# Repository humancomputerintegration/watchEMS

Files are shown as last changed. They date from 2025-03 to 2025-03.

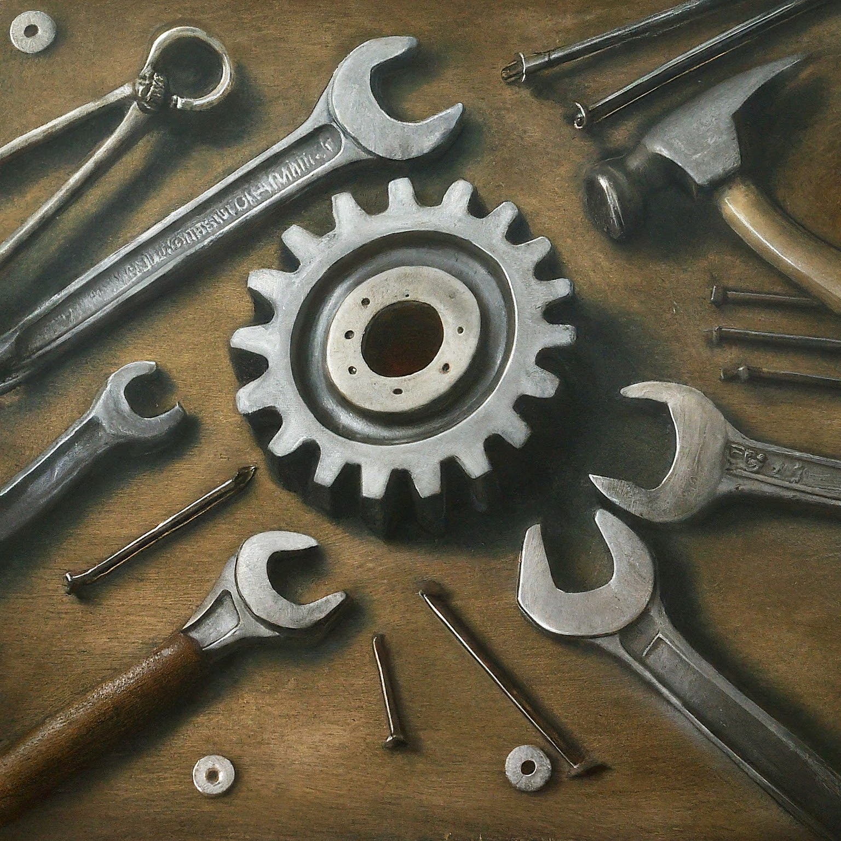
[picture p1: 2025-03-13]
codes/PCVersions/ManualCalibration/img.jpeg

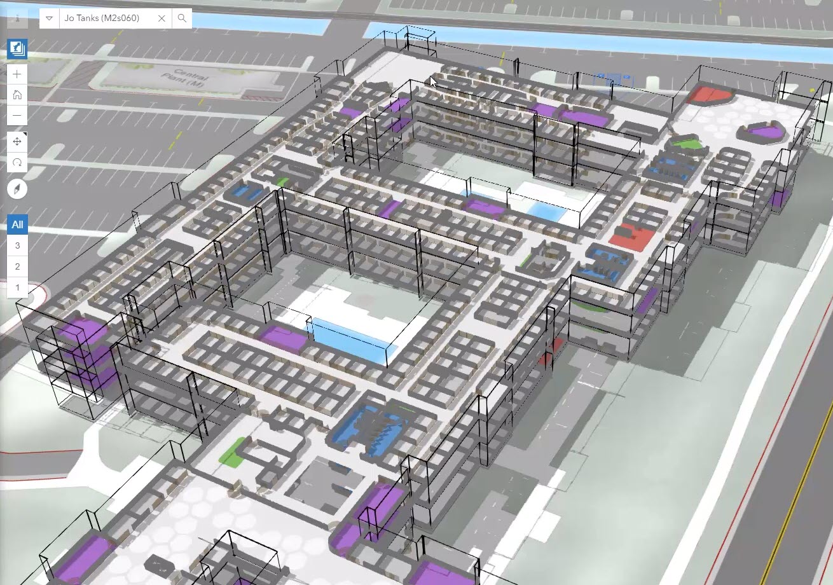
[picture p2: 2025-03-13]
codes/PCVersions/WizardOfOZMaps(Indoor)/img.jpg

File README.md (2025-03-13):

# Can a Smartwatch Move Your Fingers? 

This repository contains the source code used in the research publication "Can a Smartwatch Move Your Fingers?" from the [Human-Computer Integration Lab](https://lab.plopes.org/) at the University of Chicago.

## Citing

When using or building upon this device in an academic publication, please consider citing as follows:

ACM Reference Format: Akifumi Takahashi, Yudai Tanaka, Archit Tamhane, Alan Shen, Shan-Yuan Teng, and Pedro Lopes. 2024. Can a Smartwatch Move Your Fingers? Compact and Practical Electrical Muscle Stimulation in a Smartwatch. In The 37th Annual ACM Symposium on User Interface Software and Technology (UIST ’24), October 13–16, 2024, Pittsburgh, PA, USA. ACM, New York, NY, USA, 15 pages. https://doi.org/10.1145/3654777.3676373

## Contact

For any questions about this repository, please contact yudaitanaka@uchicago.edu

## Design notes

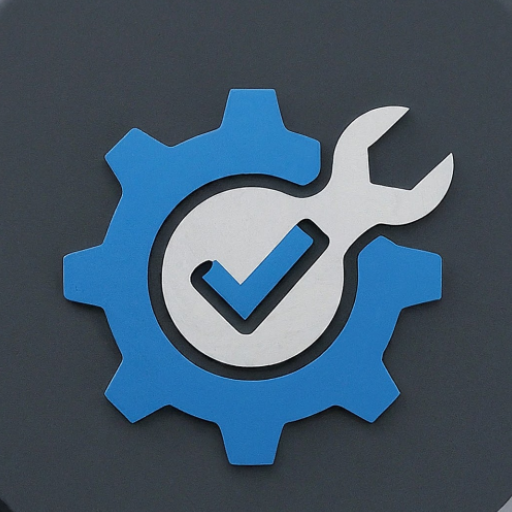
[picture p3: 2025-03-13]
codes/PCVersions/CalibApp/ic_launcher-playstore.png

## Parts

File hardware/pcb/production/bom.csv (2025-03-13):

Designator | Footprint | Quantity | Value | LCSC Part #
C1, C18 | 0402 | 2 | 1nF | C1523
C10 | 0402 | 1 | 220pF | C1530
C11, C12, C13, C14 | 0805 | 4 | 100nF | C5331016
C15, C16 | 0402 | 2 | 100nF | C9900048290
C17 | 0402 | 1 | 10uF | C408132
C19, C20 | 0603 | 2 | 4.7uF | C19666
C2, C22, C23, C3, C4, C8 | 1206 | 6 | 47uF | C76659
C21 | 0402 | 1 | 120pF | C695379
C5 | 0402 | 1 | 0.1uF | C1525
C6 | 0402 | 1 | 22nF | C1532
C7 | 0402 | 1 | 100pF | C1546
C9 | 0402 | 1 | 10nF | C15195
D1 | RF081MM2STR | 1 | RF081MM2STR | C509966
D2 | SOD2512X110N | 1 | NSVR1020MW2T1G | C893984
IC1, IC10, IC11, IC12, IC13, IC14, IC15, IC16, IC17, IC18, IC19, IC2, IC20, IC21, IC22, IC23, IC24, IC3, IC4, IC5, IC6, IC7, IC8, IC9 | SOP254P700X220-4N | 24 | TLP188_TPL,E | C4153840
IC25 | SOIC127P600X175-8N | 1 | DAC8830ID | C42816
IC26 | SOP65P640X120-14N | 1 | OPA4205APWT | C20345595
J1 | JST_GH_SM02B-GHS-TB_1x02-1MP_P1.25mm_Horizontal | 1 | Conn_01x02_Pin | C189893
J10, J8, J9 | PinHeader_1x04_P2.54mm_Vertical | 3 | Conn_01x04_Pin
J11, J12, J13, J2, J3, J4, J5, J6, J7 | Molex_200528-0070_1x07-1MP_P1.00mm_Horizontal | 9 | Conn_01x07_Pin | C6369987
JP3 | SolderJumper-2_P1.3mm_Open_TrianglePad1.0x1.5mm | 1 | Jumper_2_Open
L1 | 1008 | 1 | 4.7uH | C668313
L2 | 1008 | 1 | 1uH | C435392
Q1 | SOT95P280X100-3N | 1 | RSR030N06TL | C126317
Q2, Q4, Q5 | SOT96P237X111-3N | 3 | MMBTA92LT1G | C82049
Q3 | SOT-23 | 1 | DMN30H4D0L | C461015
R1, R2, R29, R49 | 0402 | 4 | 100k | C25741
R10, R11, R12, R13, R14, R15, R16, R17, R18, R19, R20, R21, R22, R23, R24, R25, R26, R27, R4, R5, R6, R7, R8, R9 | 0402 | 24 | 330 | C25104
R28 | 0402 | 1 | 130k(100kHz) | C409851
R3 | 0402 | 1 | 2k | C4109
R30 | 0402 | 1 | 240k | C413113
R31 | 0402 | 1 | 6.8k | C409870
R32, R34, R47 | 0402 | 3 | 22 | C413049
R33 | 0603 | 1 | 0.02 | C2088537
R35, R36, R37 | 0402 | 3 | 499k | C2986233
R38 | 0402 | 1 | 16k | C409889
R39 | 0402 | 1 | 300k | C131560
R40 | 0402 | 1 | 200k | C131534
R41 | 0402 | 1 | 1k | C445596
R42 | 0402 | 1 | 1k3 | C336808
R43 | 0402 | 1 | 100 | C491157
R44 | 0402 | 1 | 1M | C413126
R45 | 0402 | 1 | 30k | C413010
R46 | 0402 | 1 | 100 | C25077
R48 | 0402 | 1 | 453k | C27009
R50 | 0402 | 1 | 499k | C25793
T1 | ATB3225150110T000 | 1 | ATB322515-0110-T000 | C415291
U1 | SOT-23-5 | 1 | MCP73812T-420I-OT | C144308
U2 | XIAO-nRF52840-Sense-14P-2.54-21X17.8MM)_onlyPins | 1 | SeeeduinoXIAO_onlyPinHeader
U3, U4, U5 | SOP65P640X110-16N | 3 | 74AHCT595 | C554707
U6 | MSOP-10-1EP_3x3mm_P0.5mm_EP1.68x1.88mm | 1 | LT3757AEMSE | C671465
U7 | SOTFL50P160X60-6N | 1 | XPS62A01DRLR | C5157937
U8 | SOT-23-5 | 1 | TPS613222ADBV | C2071163
ffc calble | 7pin pitch1mm 30mm |  | 0152670745 |  | Molex | 0152670745 | https://www.digikey.com/en/products/detail/molex/0152670745/4427495
ffc calble | 7pin pitch1mm 50mm |  | 0152670747 |  | Molex | 0152670747 | https://www.digikey.com/en/products/detail/molex/0152670747/4427497
ffc calble | 7pin pitch1mm 70mm |  | 0151670749 |  | Molex | 0151670749 | https://www.digikey.com/en/products/detail/molex/0151670749/4426466
ffc calble | 7pin pitch1mm 76mm |  | 10-07-A-0076-C-4-08-4-T |  | GCT | 10-07-A-0076-C-4-08-4-T | https://www.digikey.jp/ja/products/detail/gct/10-07-A-0076-C-4-08-4-T/22247725
ffc calble | 7pin pitch1mm 50mm |  | 10-07-A-0050-C-4-08-4-T |  | GCT | 10-07-A-0050-C-4-08-4-T | https://www.digikey.jp/ja/products/detail/gct/10-07-A-0050-C-4-08-4-T/22247681
ffc calble | 7pin pitch1mm 152mm |  | 10-07-A-0152-C-4-08-4-T |  | GCT | 10-07-A-0152-C-4-08-4-T | https://www.digikey.jp/ja/products/detail/gct/10-07-A-0152-C-4-08-4-T/22247734
ffc calble | 7pin pitch1mm 100mm |  | 10-07-A-0101-C-4-08-4-T |  | GCT | 10-07-A-0101-C-4-08-4-T | https://www.digikey.jp/ja/products/detail/gct/10-07-A-0101-C-4-08-4-T/22247600
battery |  |  |  |  |  |  | https://www.amazon.com/gp/product/B09WK78594/ref=ppx_yo_dt_b_asin_title_o01_s00?ie=UTF8&psc=1
 |  |  | DTP401525(EZ3) |  |  |  | https://www.marutsu.co.jp/pc/i/2228265/
J1 |  |  | SM02B-SRSS-TB |  |  | SM02B-SRSS-TB | https://www.digikey.jp/ja/products/detail/jst-sales-america-inc/SM02B-SRSS-TB/926708
J1 housing |  |  | SHR-02V-S-B |  |  | SHR-02V-S-B | https://www.digikey.jp/ja/products/detail/jst-sales-america-inc/SHR-02V-S-B/759866

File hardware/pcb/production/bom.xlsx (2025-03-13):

Designator | Footprint | Quantity | Value | require | LCSC Part # |  |  |  |  | Quantity | rate | total | price/1 | price total
C1, C2, C3, C4 | CAPC2012X145N | 4 | 68nF | 200V |  | TDK | CGJ4J3X7T2D683K125AA | https://www.digikey.com/en/products/detail/tdk-corporation/CGJ4J3X7T2D683K125AA/3673570 |  | 4 | 3 | 12 | 0.64 | 7.68
C5 | 0201(0603) | 1 | 220pF | 25V |  | TDK | CGA1A2X7R1E221K030BA | https://www.digikey.com/en/products/detail/tdk-corporation/CGA1A2X7R1E221K030BA/3949331 |  | 1 | 10 | 10 | 0.1 | 1
C6 | 0201(0603) | 1 | 10nF | 25V |  | TDK | GRM033R61E103MA12D (https://www.digikey.com/en/products/detail/murata-electronics/GRM033R61E103MA12D/4904729) | https://www.digikey.com/en/products/detail/murata-electronics/GRM033R61E103MA12D/4904730 |  | 1 | 10 | 10 | 0.1 | 1
C7 | 0201(0603) | 1 | 0.1uF | 16V |  | TDK | C0603X5R1E104K030BB | https://www.digikey.com/en/products/detail/tdk-corporation/C0603X5R1E104K030BB/3950907 |  | 1 | 10 | 10 | 0.1 | 1
C8 | 0201(0603) | 1 | 22nF | 16V |  | TDK | C0603X5R1E223K030BB | https://www.digikey.com/en/products/detail/tdk-corporation/C0603X5R1E223K030BB/3950911 |  | 1 | 10 | 10 | 0.1 | 1
C9 | 0201(0603) | 1 | 1nF | 16V |  | TDK | C0603X7R1E102K030BA | https://www.digikey.com/en/products/detail/tdk-corporation/C0603X7R1E102K030BA/2732710 |  | 1 | 10 | 10 | 0.1 | 1
D1 | RF081MM2STR | 1 | RF081MM2STR | 200V |  | Rohm Semiconductor | RF081MM2STR | https://www.digikey.com/en/products/detail/rohm-semiconductor/RF081MM2STR/5001871 | 200V 800MA | 1 | 3 | 3 | 0.48 | 1.44
IC1, IC10, IC11, IC12, IC13, IC14, IC15, IC16, IC17, IC18, IC19, IC2, IC20, IC21, IC22, IC23, IC24, IC25, IC26, IC27, IC28, IC29, IC3, IC30, IC31, IC32, IC4, IC5, IC6, IC7, IC8, IC9 | SOP254P700X220-4N | 32 | TLP188_TPL,E | 200V |  | Toshiba Semiconductor and Storage | TLP188(TPL,E | https://www.digikey.com/en/products/detail/toshiba-semiconductor-and-storage/TLP188-TPL-E/4562859 | OPTOISO 3.75KV TRANS 6-SO 4 LEAD | 32 | 1 | 32 | 0.81 | 25.92
IC33 | SOIC127P599X175-8N | 1 | LT1013DS8#TRPBF |  |  | Analog Devices Inc. | LT1013DS8#TRPBF | https://www.digikey.com/en/products/detail/analog-devices-inc/LT1013DS8-TRPBF/960372 |  | 1 | 3 | 3 | 7.28 | 21.84
J1, J11, J12, J14, J3, J5, J6, J8, J9 | Molex_200528-0070_1x07-1MP_P1.00mm_Horizontal | 9 | Conn_01x07_Pin |  |  | Molex | 2005280070 | https://www.digikey.com/en/products/detail/molex/2005280070/6099557 |  | 9 | 3 | 27 | 0.6 | 16.2
J10, J15, J2, J4, J7 | PinHeader_1x04_P2.54mm_Vertical | 5 | Conn_01x04_Pin |  |  |  |  |  |  | 5 | 3 | 15 |  | 0
JP1 | SolderJumper-2_P1.3mm_Open_TrianglePad1.0x1.5mm | 1 | Jumper_2_Open |  |  |  |  |  |  | 1 | 3 | 3 |  | 0
JP2 | SolderJumper-3_P2.0mm_Open_TrianglePad1.0x1.5mm_NumberLabels | 1 | Jumper_3_Open |  |  |  |  |  |  | 1 | 3 | 3 |  | 0
Q1 | SOT95P280X100-3N | 1 | RQ5E030AJTCL -> SSM3K376R,LF | 30V |  | Toshiba Semiconductor and Storage | SSM3K376R,LF | https://www.digikey.com/en/products/detail/toshiba-semiconductor-and-storage/SSM3K376R-LF/9472331?s=N4IgTCBcDaIMpwLIGYDSyDsA2ASgGgBkAxEAXQF8g | 30V4A | 1 | 3 | 3 | 0.38 | 1.14
Q2 | SOT-23 | 1 | DMN24H11DS | 200V |  | Diodes Incorporated | DMN24H11DS-7 | https://www.digikey.com/en/products/detail/diodes-incorporated/DMN24H11DS-7/9770107 |  | 1 | 3 | 3 | 0.44 | 1.32
Q3, Q4, Q5 | SOT96P237X111-3N | 3 | MMBTA92LT1G | 200V |  | onsemi | MMBTA92LT3G | https://www.digikey.com/en/products/detail/onsemi/MMBTA92LT3G/1481979 | TRANS PNP 300V 0.5A SOT23-3 | 3 | 3 | 9 | 0.21 | 1.89
R1 | 0201(0603) | 1 | 100k | 1.1e-4W |  | Panasonic Electronic Components | ERJ-1GNF1003C | https://www.digikey.com/en/products/detail/panasonic-electronic-components/ERJ-1GNF1003C/2036340?s=N4IgTCBcDaIKICUBSBaAjAcQHIDE0AZ8BmAYRAF0BfIA |  | 1 | 10 | 10 | 0.1 | 1
R10, R11, R12, R13, R14, R15, R16, R17, R18, R19, R20, R21, R22, R23, R24, R25, R26, R27, R28, R29, R30, R31, R32, R33, R34, R35, R36, R37, R38, R39, R40, R41 | 0201(0603) | 32 | 470 -> 220 |  |  | Panasonic Electronic Components | ERJ-1GNF4700C | https://www.digikey.com/en/products/detail/panasonic-electronic-components/erj-1gnf2200c/2036034 |  | 32 | 2 | 64 | 0.1 | 6.4
R2, R4 | 0201(0603) | 2 | 22 | 1e-5W |  | Panasonic Electronic Components | ERJ-1GNF22R0C | https://www.digikey.com/en/products/detail/panasonic-electronic-components/ERJ-1GNF22R0C/2035920 | RES SMD 22 OHM 1% 1/20W 0201 | 2 | 10 | 20 | 0.1 | 2
R3 | 0201(0603) | 1 | 47k |  |  | Panasonic Electronic Components | ERJ-1GNF4702C | https://www.digikey.com/en/products/detail/panasonic-electronic-components/ERJ-1GNF4702C/2036302 |  | 1 | 10 | 10 | 0.1 | 1
R42 | 0201(0603) | 1 | 3,3k | 0.024W |  | Panasonic Electronic Components | ERJ-1GNF3301C | https://www.digikey.com/en/products/detail/panasonic-electronic-components/ERJ-1GNF3301C/2036169 |  | 1 | 10 | 10 | 0.1 | 1
R43 | 0201(0603) | 1 | 10k | 0.01W(MOSFET broken 0.066W) |  | Panasonic Electronic Components | ERJ-1GNF1002C (https://www.digikey.com/en/products/detail/panasonic-electronic-components/ERJ-1GNF1002C/2036226) | https://www.digikey.com/en/products/detail/panasonic-electronic-components/ERJ-1GNF1002C/2036226 |  | 1 | 10 | 10 | 0.1 | 1
R44 | 0603 (1608) | 1 | 1k | 0.1W |  | Panasonic Electronic Components | ERJ-PB3D1001V | https://www.digikey.com/en/products/detail/panasonic-electronic-components/ERJ-PB3D1001V/6213066 | 2 kOhms ±0.5% 0.2W, 1/5W Chip Resistor 0603 (1608 Metric) Automotive AEC-Q200, Pulse Withstanding Thick Film | 1 | 10 | 10 | 0.16 | 1.6
R45, R5 | 0402 (1005) | 2 | 1M | 0.01W |  | Panasonic Electronic Components | ERJ-2RKF1004X | https://www.digikey.com/en/products/detail/panasonic-electronic-components/ERJ-2RKF1004X/79728 |  | 2 | 10 | 20 | 0.1 | 2
R46 | 0201(0603) | 1 | 25k -> 30k | 2.37e-4W |  | Panasonic Electronic Components | ERJ-1GNF3002C | https://www.digikey.com/en/products/detail/panasonic-electronic-components/ERJ-1GNF3002C/2036278 |  | 1 | 10 | 10 | 0.1 | 1
R47 | 0201(0603) | 1 | 100 |  |  | Panasonic Electronic Components | ERJ-1GNF1000C | https://www.digikey.com/en/products/detail/panasonic-electronic-components/ERJ-1GNF1000C/2035998 |  | 1 | 10 | 10 | 0.1 | 1
R6 | 0201(0603) | 1 | 6.8k |  |  | Panasonic Electronic Components | ERJ-1GNF6801C | https://www.digikey.com/en/products/detail/panasonic-electronic-components/ERJ-1GNF6801C/2036207 |  | 1 | 10 | 10 | 0.1 | 1
R7 | 0603 (1608) | 1 | 0.02 | 1/3W |  | Panasonic Electronic Components | ERJ-3BWFR020V | https://www.digikey.com/en/products/detail/panasonic-electronic-components/ERJ-3BWFR020V/5647494 | 20 mOhms ±1% 0.333W, 1/3W Chip Resistor 0603 (1608 Metric) | 1 | 10 | 10 | 0.36 | 3.6
R8 | 0201(0603) | 1 | 16k | 2.5e-6W |  | Panasonic Electronic Components | ERJ-1GNF1602C | https://www.digikey.com/en/products/detail/panasonic-electronic-components/ERJ-1GNF1602C/2036247 |  | 1 | 10 | 10 | 0.1 | 1
R9 | 0201(0603) | 1 | 130k(100kHz) or 41.2k(300kHz) |  |  | Panasonic Electronic Components | ERJ-1GNF1303C | https://www.digikey.com/en/products/detail/panasonic-electronic-components/ERJ-1GNF1303C/2036352 |  | 1 | 10 | 10 | 0.1 | 1
T1 | ATB3225150110T000 | 1 | ATB322515-0110-T000 |  |  | TDK | ATB322515-0110 | https://www.digikey.com/en/products/detail/tdk-corporation/ATB322515-0110/3008141?s=N4IgTCBcDaIIIBUBCBmMYCsBGDBaADFlvrgvuSALoC%2BQA |  | 1 | 3 | 3 | 2.12 | 6.36
U1 | MSOP-10-1EP_3x3mm_P0.5mm_EP1.68x1.88mm | 1 | LT3757AEMSE |  |  | Analog Devices Inc. | LT3757AEMSE#TRPBF | https://www.digikey.com/en/products/detail/analog-devices-inc/LT3757AEMSE-TRPBF/3838478 |  | 1 | 3 | 3 | 6.66 | 19.98
U2 | XIAO-nRF52840-Sense-14P-2.54-21X17.8MM)_onlyPins | 1 | SeeeduinoXIAO_onlyPinHeader |  |  |  |  |  |  | 1 | 3 | 3 |  | 0
U3, U4, U5, U6 | SOP65P640X110-16N | 4 | 74AHCT595 |  |  | Nexperia USA Inc. | 74AHCT595PW,118 | https://www.digikey.com/en/products/detail/nexperia-usa-inc/74AHCT595PW-118/1229738 |  | 4 | 3 | 12 | 0.58 | 6.96
ffc calble | 7pin pitch1mm 30mm | 4 | 0152670745 |  |  | Molex | 0152670745 | https://www.digikey.com/en/products/detail/molex/0152670745/4427495 |  | 4 | 3 | 12 | 1.41 | 16.92
ffc calble | 7pin pitch1mm 50mm | 4 | 0152670747 |  |  | Molex | 0152670747 | https://www.digikey.com/en/products/detail/molex/0152670747/4427497 |  | 4 | 3 | 12 | 1.62 | 19.44
ffc calble | 7pin pitch1mm 70mm | 4 | 0151670749 |  |  | Molex | 0151670749 | https://www.digikey.com/en/products/detail/molex/0151670749/4426466 |  | 4 | 3 | 12 | 1.35 | 16.2
 |  |  |  |  |  |  |  |  |  |  |  |  |  | 192.89

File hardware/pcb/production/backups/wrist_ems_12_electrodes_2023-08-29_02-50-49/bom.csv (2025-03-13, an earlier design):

Designator | Footprint | Quantity | Value | LCSC Part #
C1, C2, C3, C4 | CAPC2012X145N | 4 | 68nF
C5 | 0201 | 1 | 220pF
C6 | 0201 | 1 | 10nF
C7 | 0201 | 1 | 0.1uF
C8 | 0201 | 1 | 22nF
C9 | 0201 | 1 | 1nF
D1 | RF081MM2STR | 1 | RF081MM2STR
IC1, IC10, IC11, IC12, IC13, IC14, IC15, IC16, IC17, IC18, IC19, IC2, IC20, IC21, IC22, IC23, IC24, IC25, IC26, IC27, IC28, IC29, IC3, IC30, IC31, IC32, IC4, IC5, IC6, IC7, IC8, IC9 | SOP254P700X220-4N | 32 | TLP188_TPL,E
IC33 | SOIC127P599X175-8N | 1 | LT1013DS8#TRPBF
J1, J11, J12, J14, J3, J5, J6, J8, J9 | Molex_200528-0070_1x07-1MP_P1.00mm_Horizontal | 9 | Conn_01x07_Pin
J10, J15, J2, J4, J7 | PinHeader_1x04_P2.54mm_Vertical | 5 | Conn_01x04_Pin
JP1 | SolderJumper-2_P1.3mm_Open_TrianglePad1.0x1.5mm | 1 | Jumper_2_Open
JP2 | SolderJumper-3_P2.0mm_Open_TrianglePad1.0x1.5mm_NumberLabels | 1 | Jumper_3_Open
Q1 | SOT95P280X100-3N | 1 | RQ5E030AJTCL
Q2 | SOT-23 | 1 | DMN24H11DS
Q3, Q4, Q5 | SOT96P237X111-3N | 3 | MMBTA92LT1G
R1 | 0201 | 1 | 100k
R10, R11, R12, R13, R14, R15, R16, R17, R18, R19, R20, R21, R22, R23, R24, R25, R26, R27, R28, R29, R30, R31, R32, R33, R34, R35, R36, R37, R38, R39, R40, R41 | 0201 | 32 | 470
R2, R4 | 0201 | 2 | 22
R3 | 0201 | 1 | 47k
R42 | 0201 | 1 | 3,3k
R43 | 0201 | 1 | 10k
R44 | 0201 | 1 | 1k
R45, R5 | 0201 | 2 | 1M
R46 | 0201 | 1 | 25k
R47 | 0201 | 1 | 100
R6 | 0201 | 1 | 6.8k
R7 | 0201 | 1 | 0.02
R8 | 0201 | 1 | 16k
R9 | 0201 | 1 | 130k(100kHz) or 41.2k(300kHz)
T1 | ATB3225150110T000 | 1 | ATB322515-0110-T000
U1 | MSOP-10-1EP_3x3mm_P0.5mm_EP1.68x1.88mm | 1 | LT3757AEMSE
U2 | XIAO-nRF52840-Sense-14P-2.54-21X17.8MM)_onlyPins | 1 | SeeeduinoXIAO_onlyPinHeader
U3, U4, U5, U6 | SOP65P640X110-16N | 4 | 74AHCT595

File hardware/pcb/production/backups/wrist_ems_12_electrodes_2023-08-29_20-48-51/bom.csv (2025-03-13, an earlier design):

Designator | Footprint | Quantity | Value | LCSC Part #
C1 | 0201 | 1 | 0.1uF
C2 | 0201 | 1 | 22nF
C3 | 0201 | 1 | 1nF
C4 | 0201 | 1 | 220pF
C5 | 0201 | 1 | 10nF
C6, C7, C8, C9 | CAPC2012X145N | 4 | 68nF
D1 | RF081MM2STR | 1 | RF081MM2STR
IC1 | SOIC127P599X175-8N | 1 | LT1013DS8#TRPBF
IC10, IC11, IC12, IC13, IC14, IC15, IC16, IC17, IC18, IC19, IC2, IC20, IC21, IC22, IC23, IC24, IC25, IC26, IC27, IC28, IC29, IC3, IC30, IC31, IC32, IC33, IC4, IC5, IC6, IC7, IC8, IC9 | SOP254P700X220-4N | 32 | TLP188_TPL,E
J1, J11, J12, J13, J14, J3, J4, J5, J6 | Molex_200528-0070_1x07-1MP_P1.00mm_Horizontal | 9 | Conn_01x07_Pin
J10, J2, J7, J8, J9 | PinHeader_1x04_P2.54mm_Vertical | 5 | Conn_01x04_Pin
JP1 | SolderJumper-2_P1.3mm_Open_TrianglePad1.0x1.5mm | 1 | Jumper_2_Open
JP2 | SolderJumper-3_P2.0mm_Open_TrianglePad1.0x1.5mm_NumberLabels | 1 | Jumper_3_Open
Q1 | SOT95P280X100-3N | 1 | RQ5E030AJTCL
Q2, Q4, Q5 | SOT96P237X111-3N | 3 | MMBTA92LT1G
Q3 | SOT-23 | 1 | DMN24H11DS
R1 | 0201 | 1 | 130k(100kHz) or 41.2k(300kHz)
R10 | 0603 | 1 | 0.02
R11 | 0603 | 1 | 1k
R12 | 0402 | 1 | 1M
R13 | 0201 | 1 | 25k
R14 | 0201 | 1 | 1M
R15 | 0201 | 1 | 16k
R16, R17, R18, R19, R20, R21, R22, R23, R24, R25, R26, R27, R28, R29, R30, R31, R32, R33, R34, R35, R36, R37, R38, R39, R40, R41, R42, R43, R44, R45, R46, R47 | 0201 | 32 | 470
R2 | 0201 | 1 | 100k
R3 | 0201 | 1 | 47k
R4 | 0201 | 1 | 6.8k
R5 | 0201 | 1 | 100
R6, R7 | 0201 | 2 | 22
R8 | 0201 | 1 | 10k
R9 | 0201 | 1 | 3,3k
T1 | ATB3225150110T000 | 1 | ATB322515-0110-T000
U1 | MSOP-10-1EP_3x3mm_P0.5mm_EP1.68x1.88mm | 1 | LT3757AEMSE
U2 | XIAO-nRF52840-Sense-14P-2.54-21X17.8MM)_onlyPins | 1 | SeeeduinoXIAO_onlyPinHeader
U3, U4, U5, U6 | SOP65P640X110-16N | 4 | 74AHCT595

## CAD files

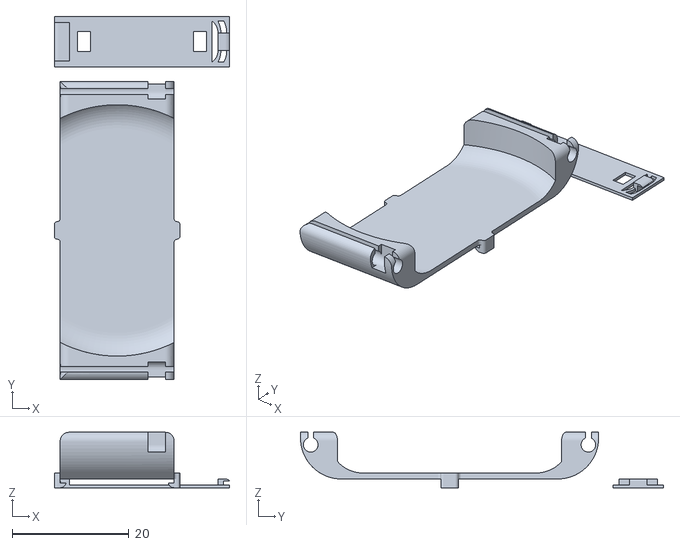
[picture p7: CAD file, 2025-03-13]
hardware/3dprinting/watch_mount v5.stl
30.0 x 62.1 x 9.50

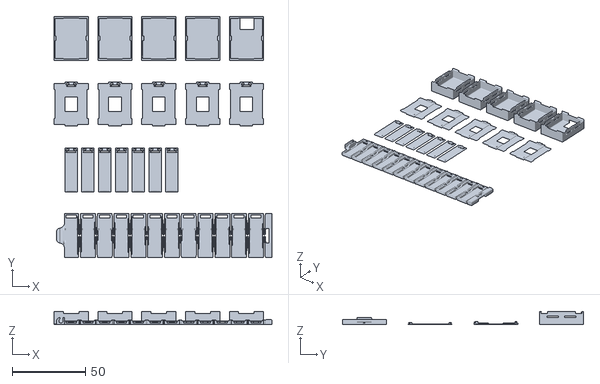
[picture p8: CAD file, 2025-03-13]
hardware/3dprinting/wristband_expandable_146.5(mm) v16.stl
149.2 x 165.0 x 9.00

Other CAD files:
hardware/3dprinting/watch_mount v4.stl
hardware/3dprinting/watch_mount v5.f3d
hardware/3dprinting/wristband_expandable_146.5(mm) v16.f3d

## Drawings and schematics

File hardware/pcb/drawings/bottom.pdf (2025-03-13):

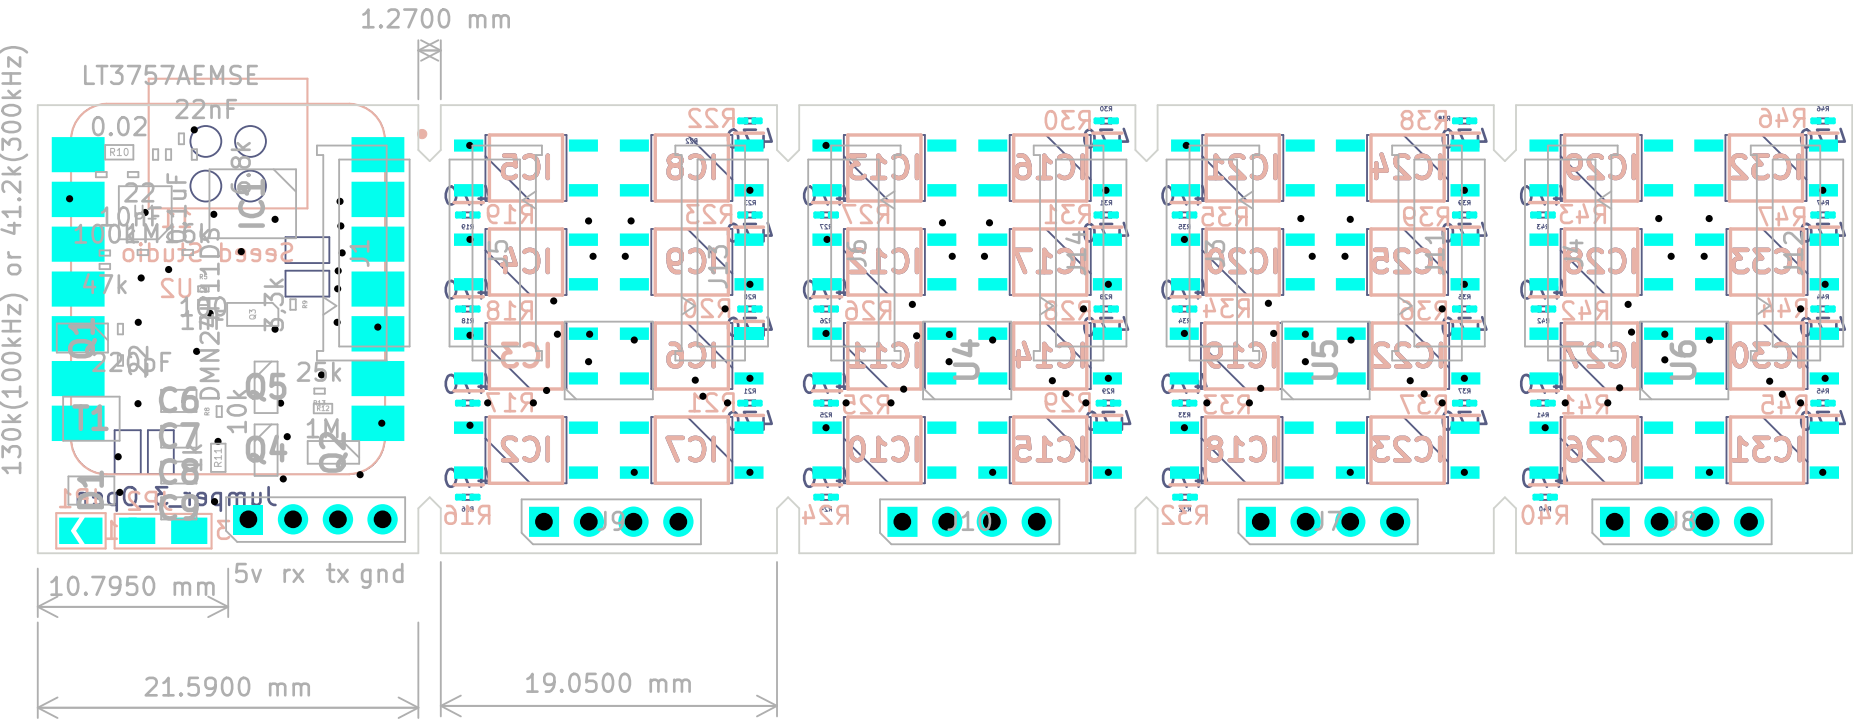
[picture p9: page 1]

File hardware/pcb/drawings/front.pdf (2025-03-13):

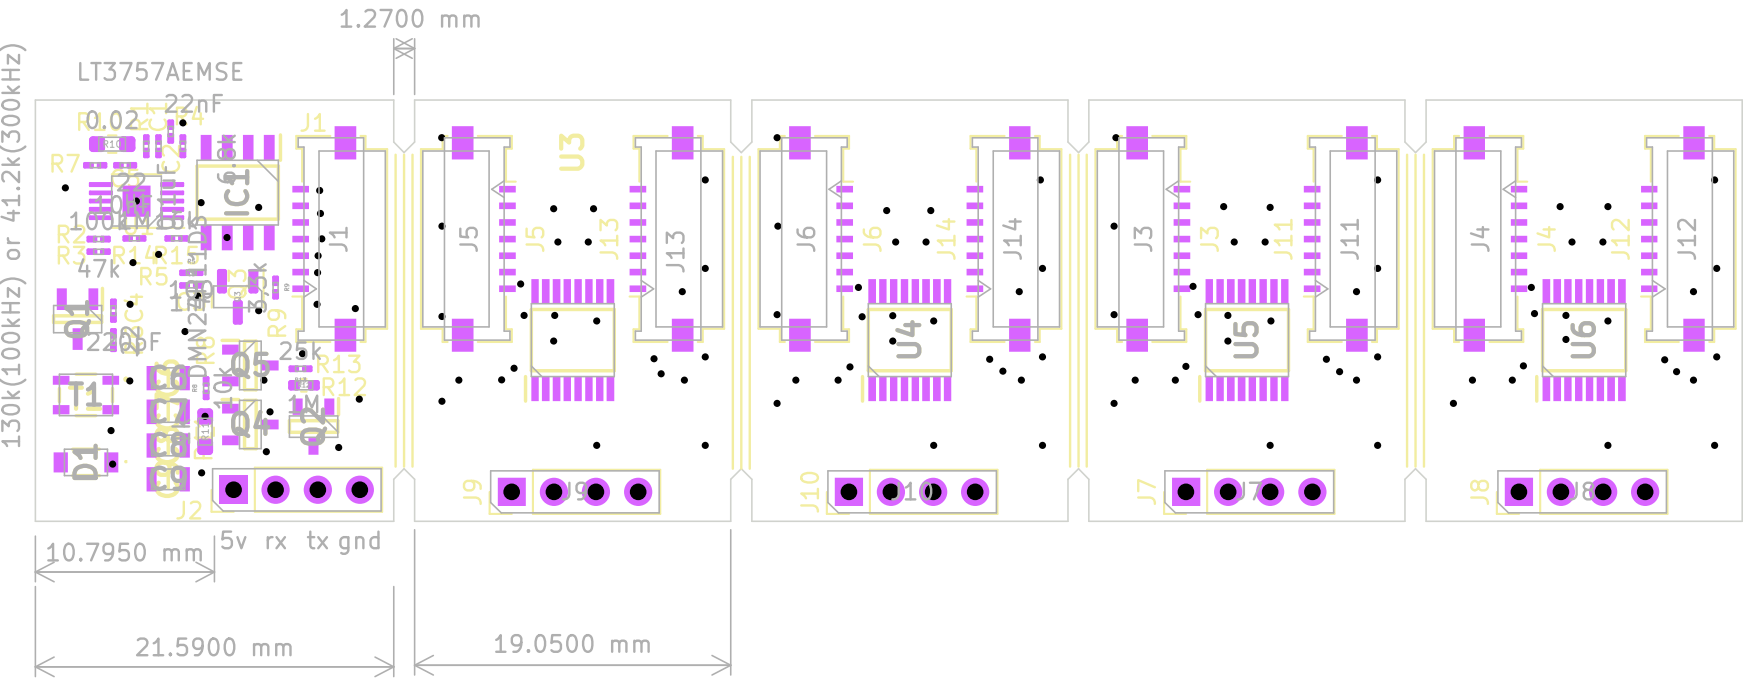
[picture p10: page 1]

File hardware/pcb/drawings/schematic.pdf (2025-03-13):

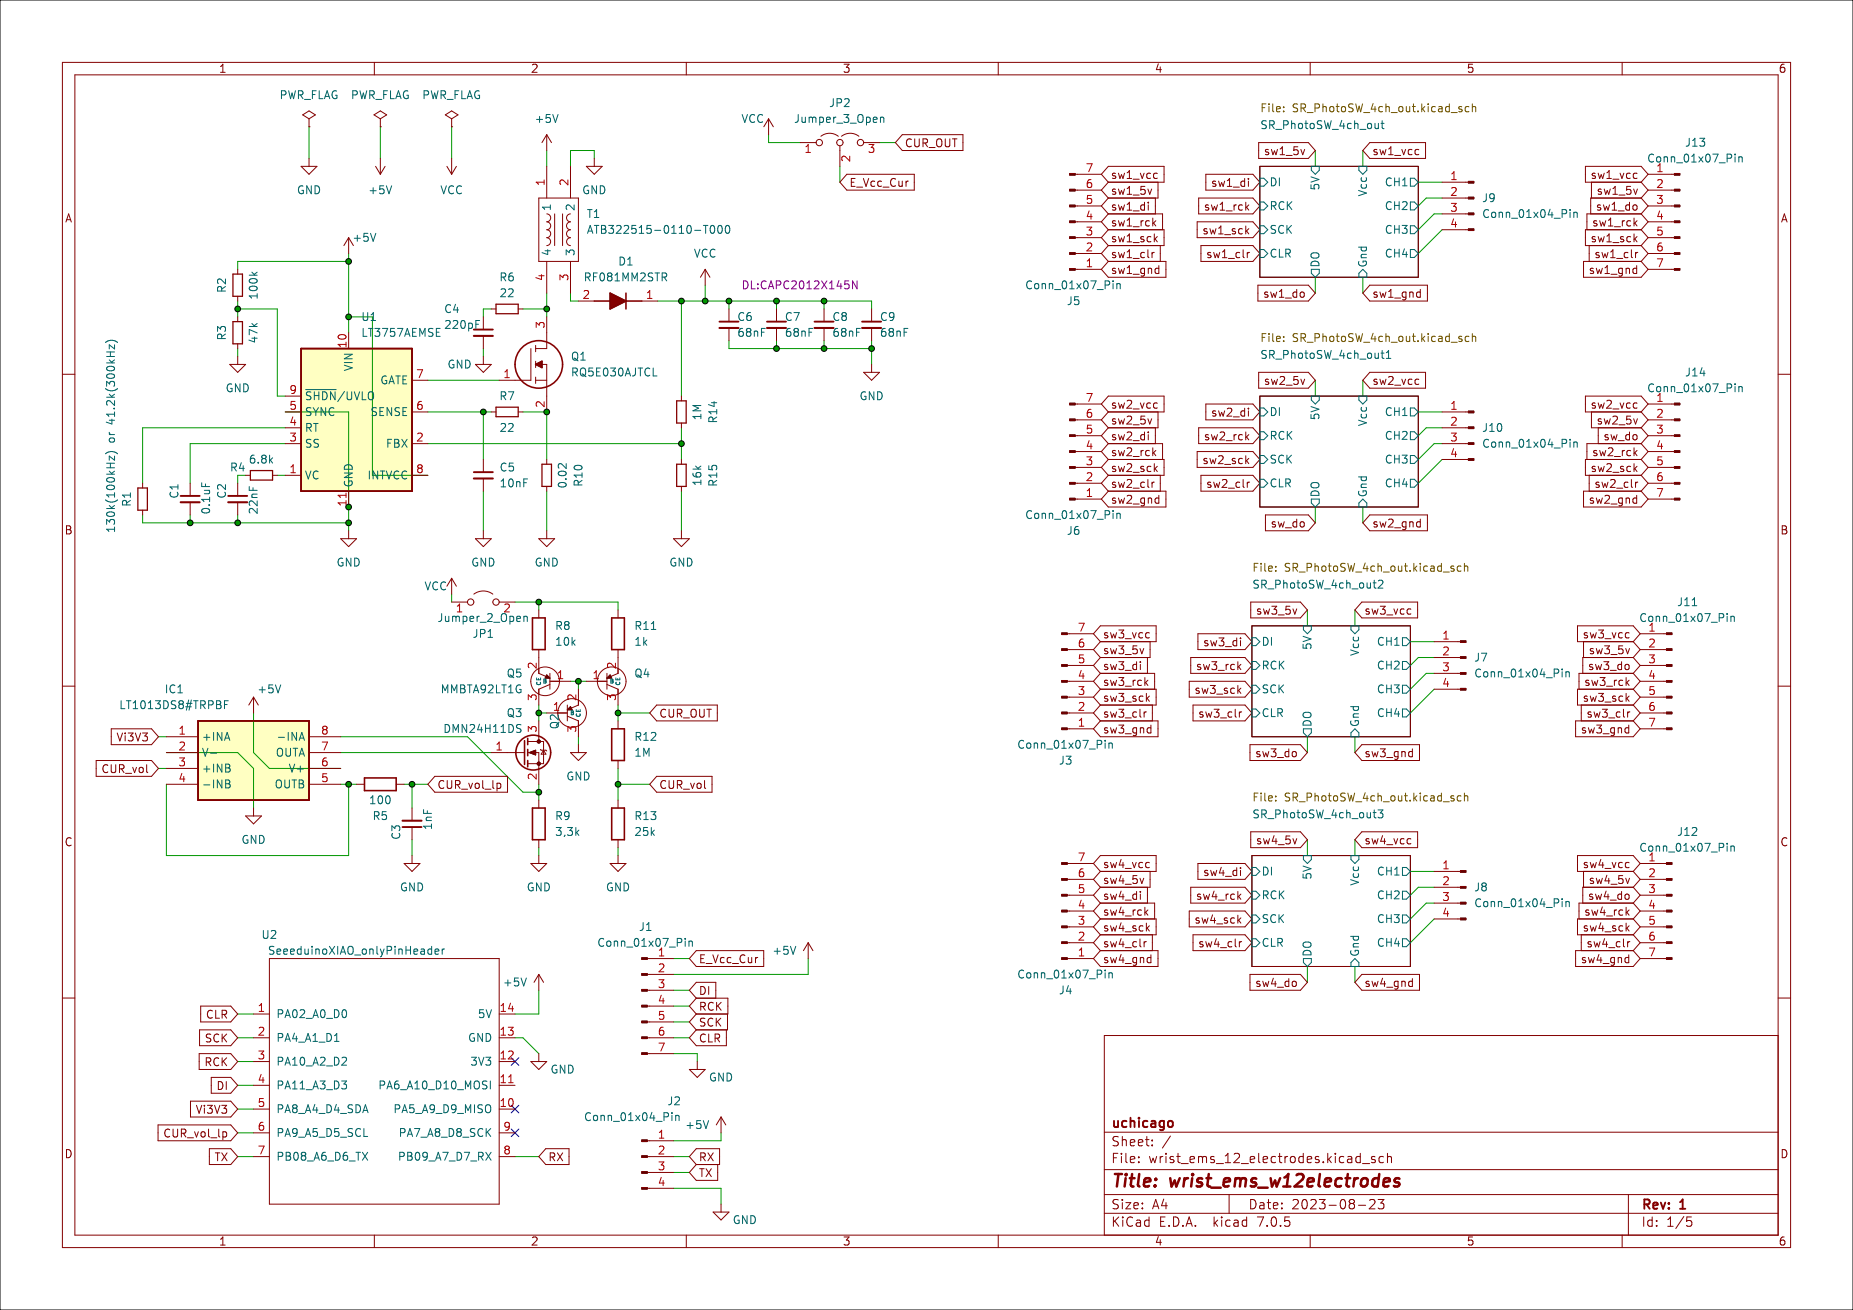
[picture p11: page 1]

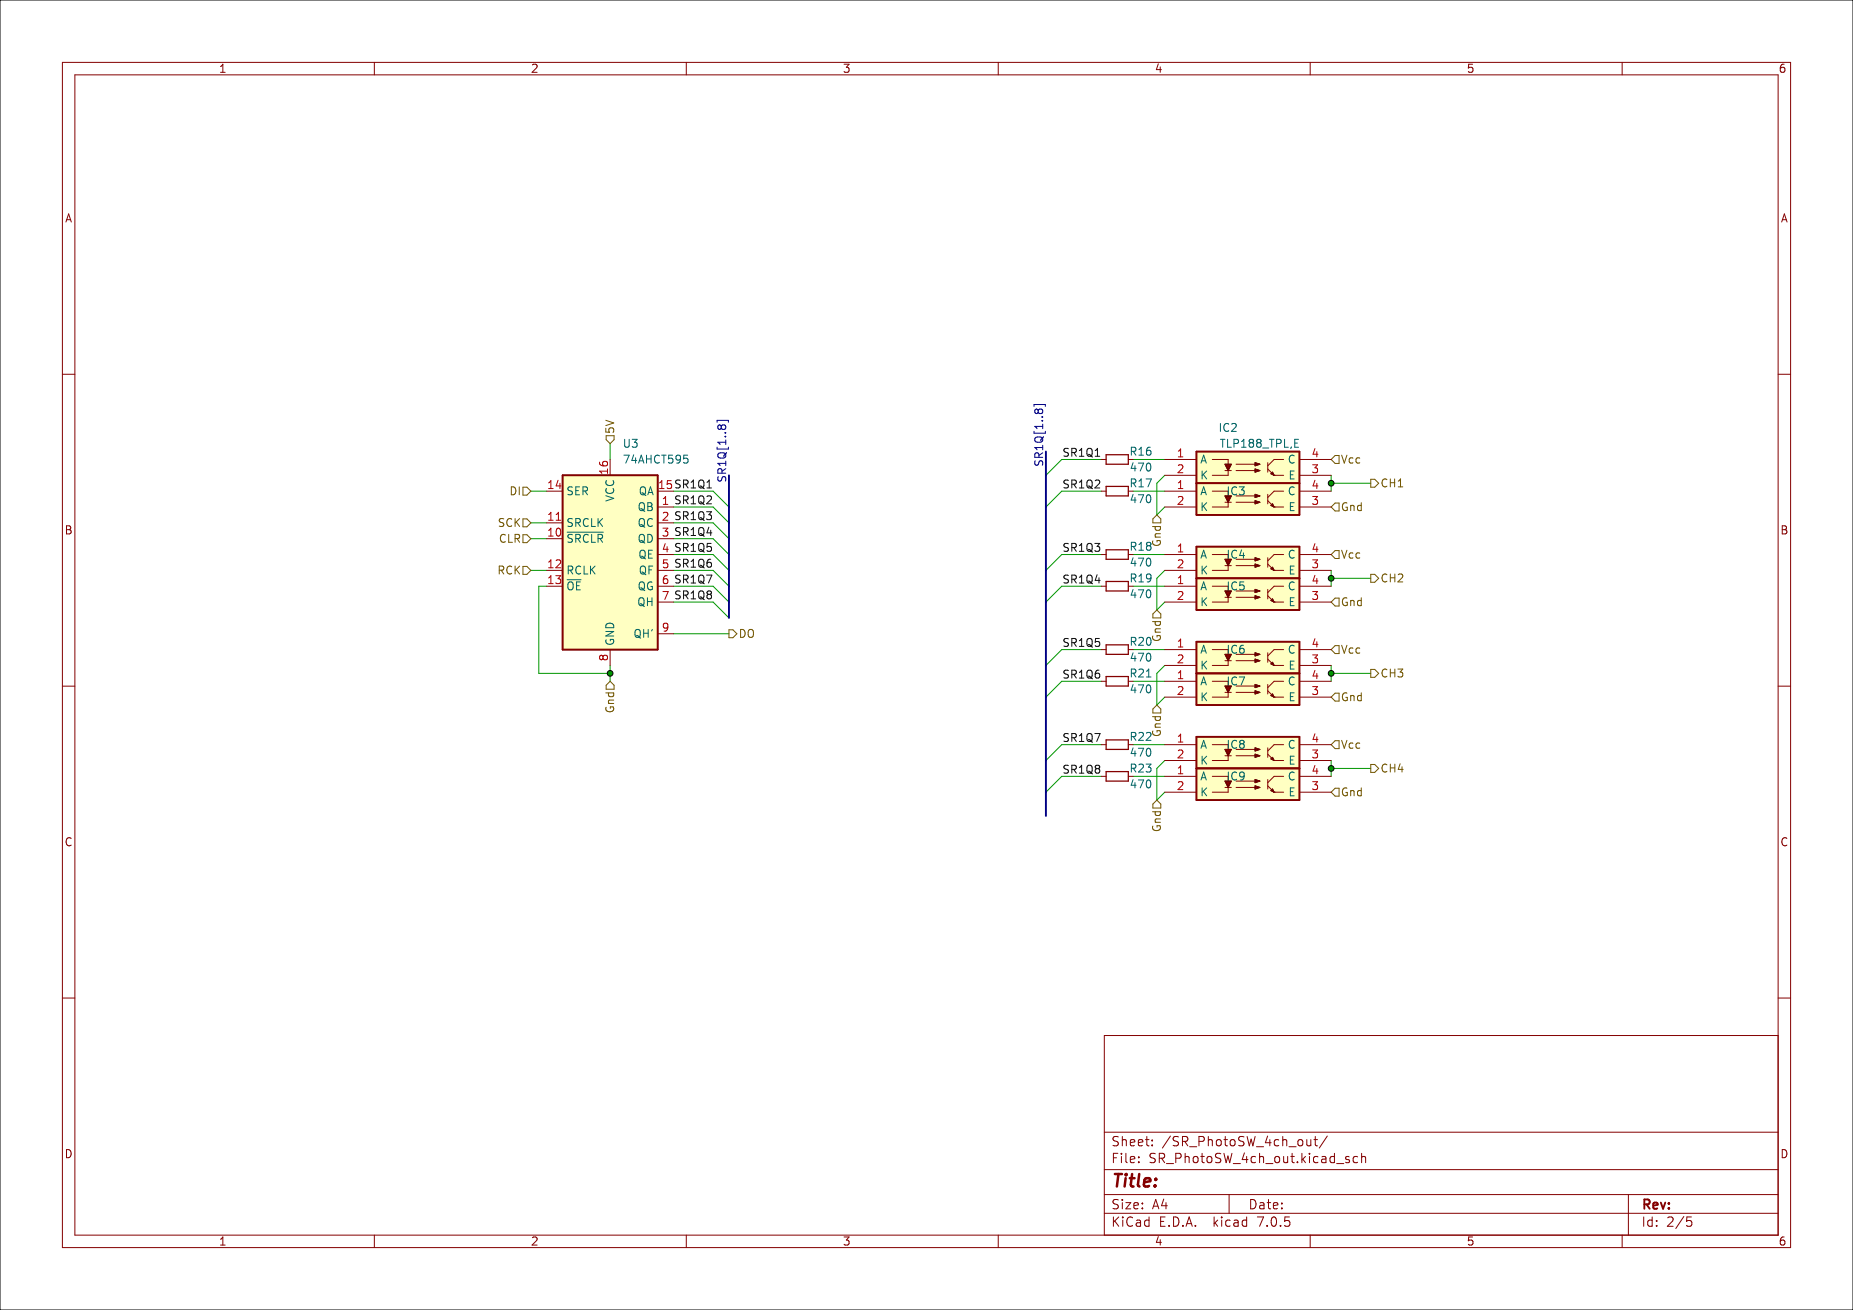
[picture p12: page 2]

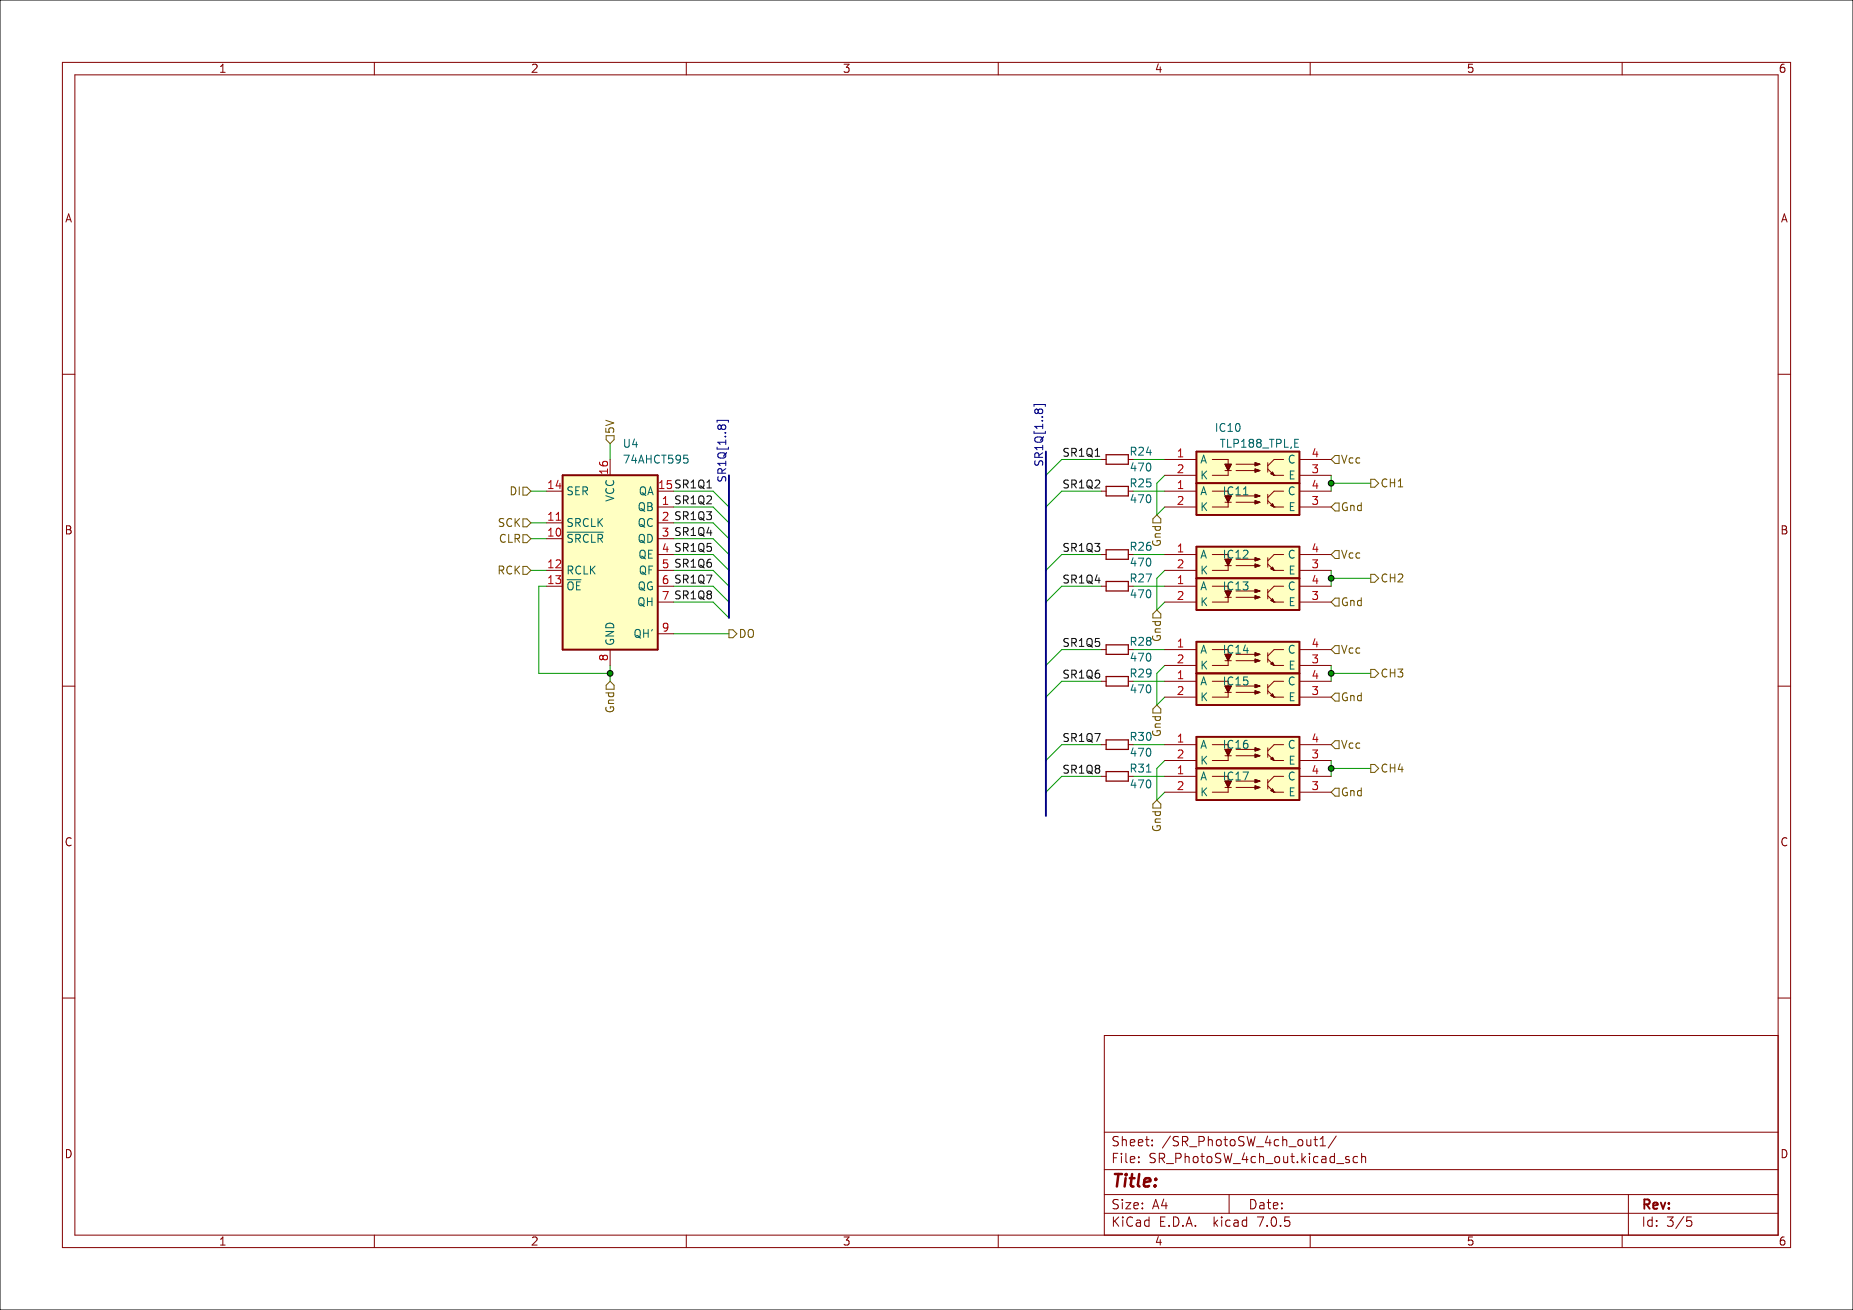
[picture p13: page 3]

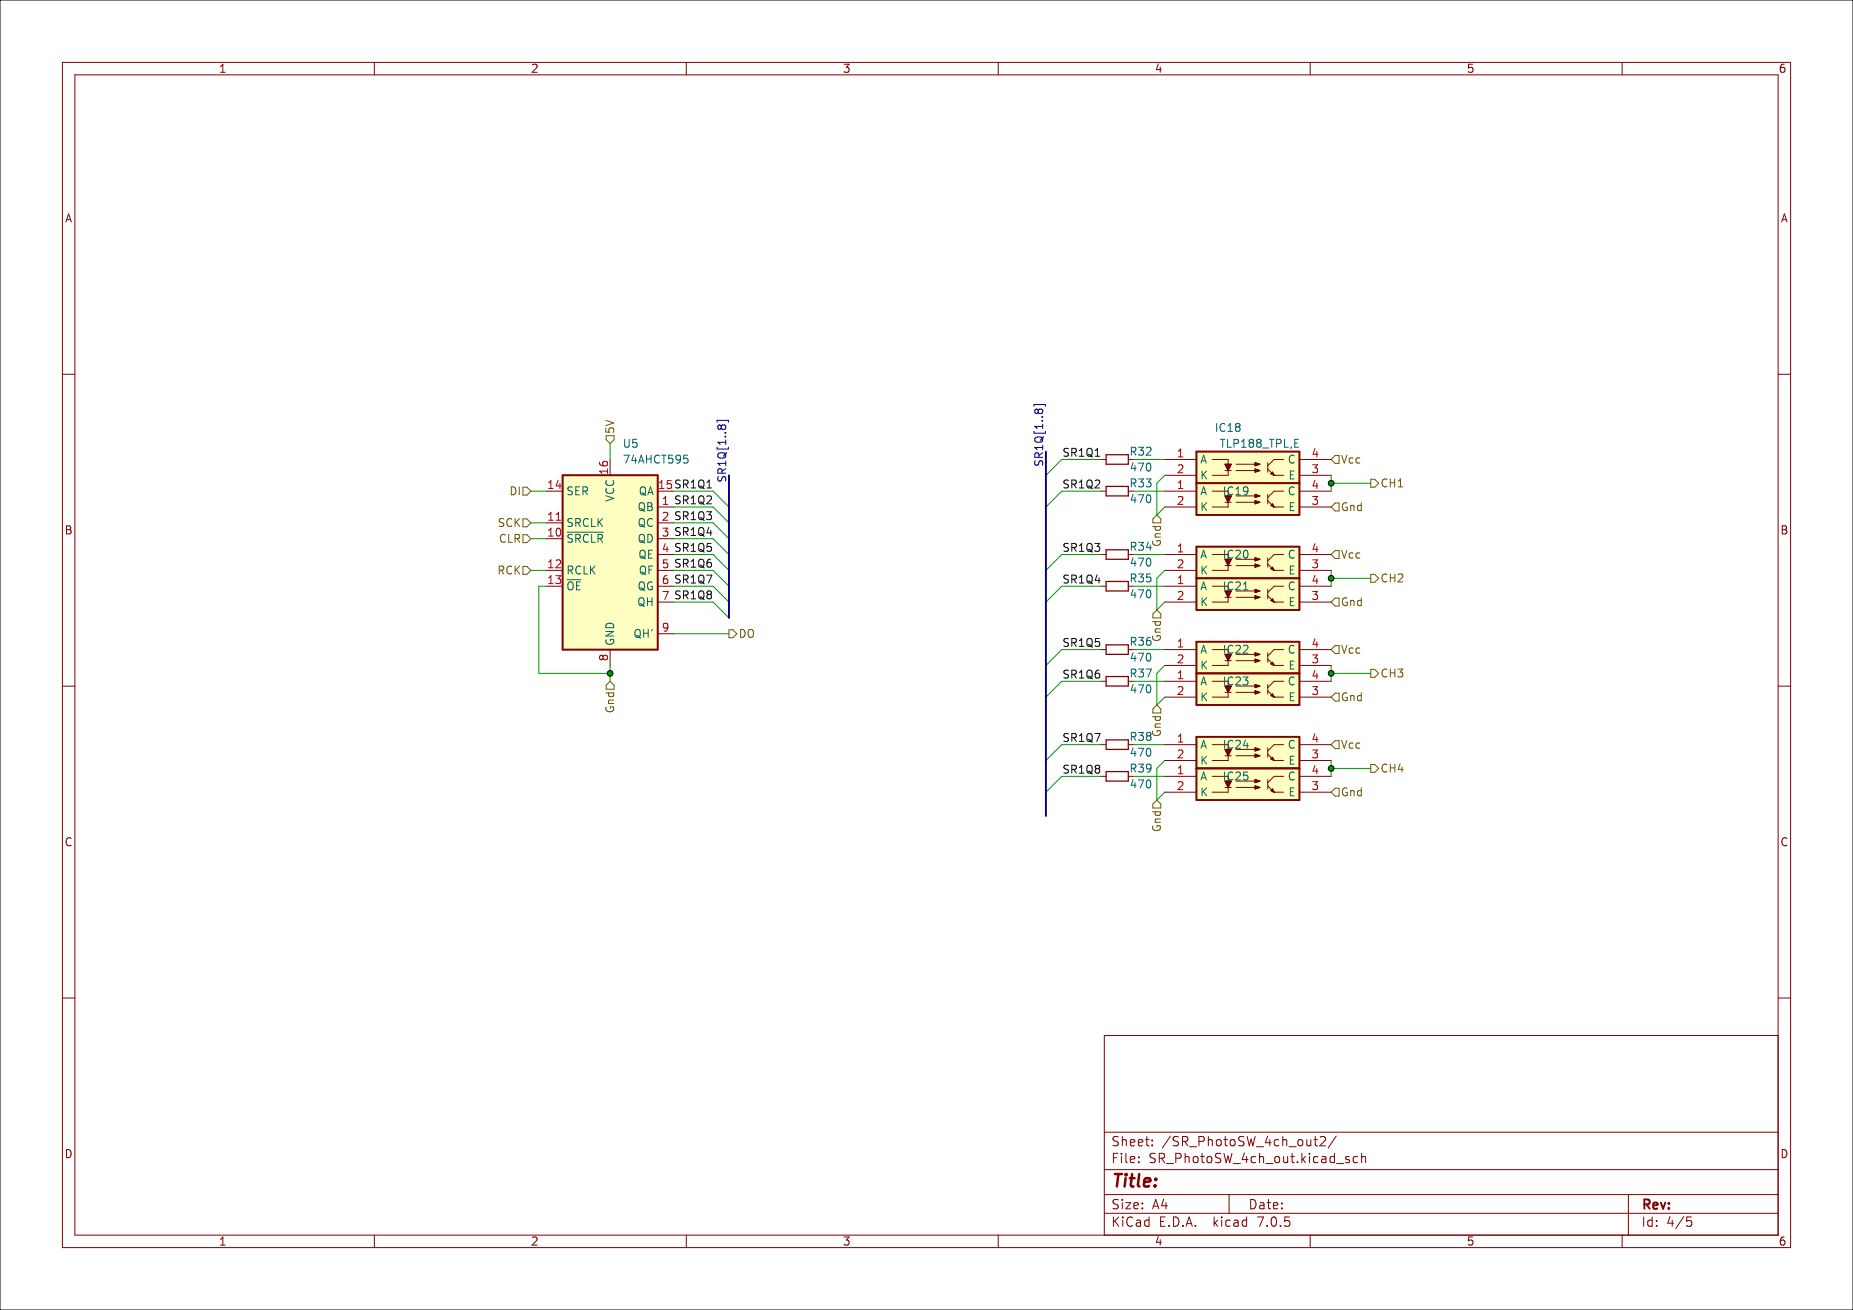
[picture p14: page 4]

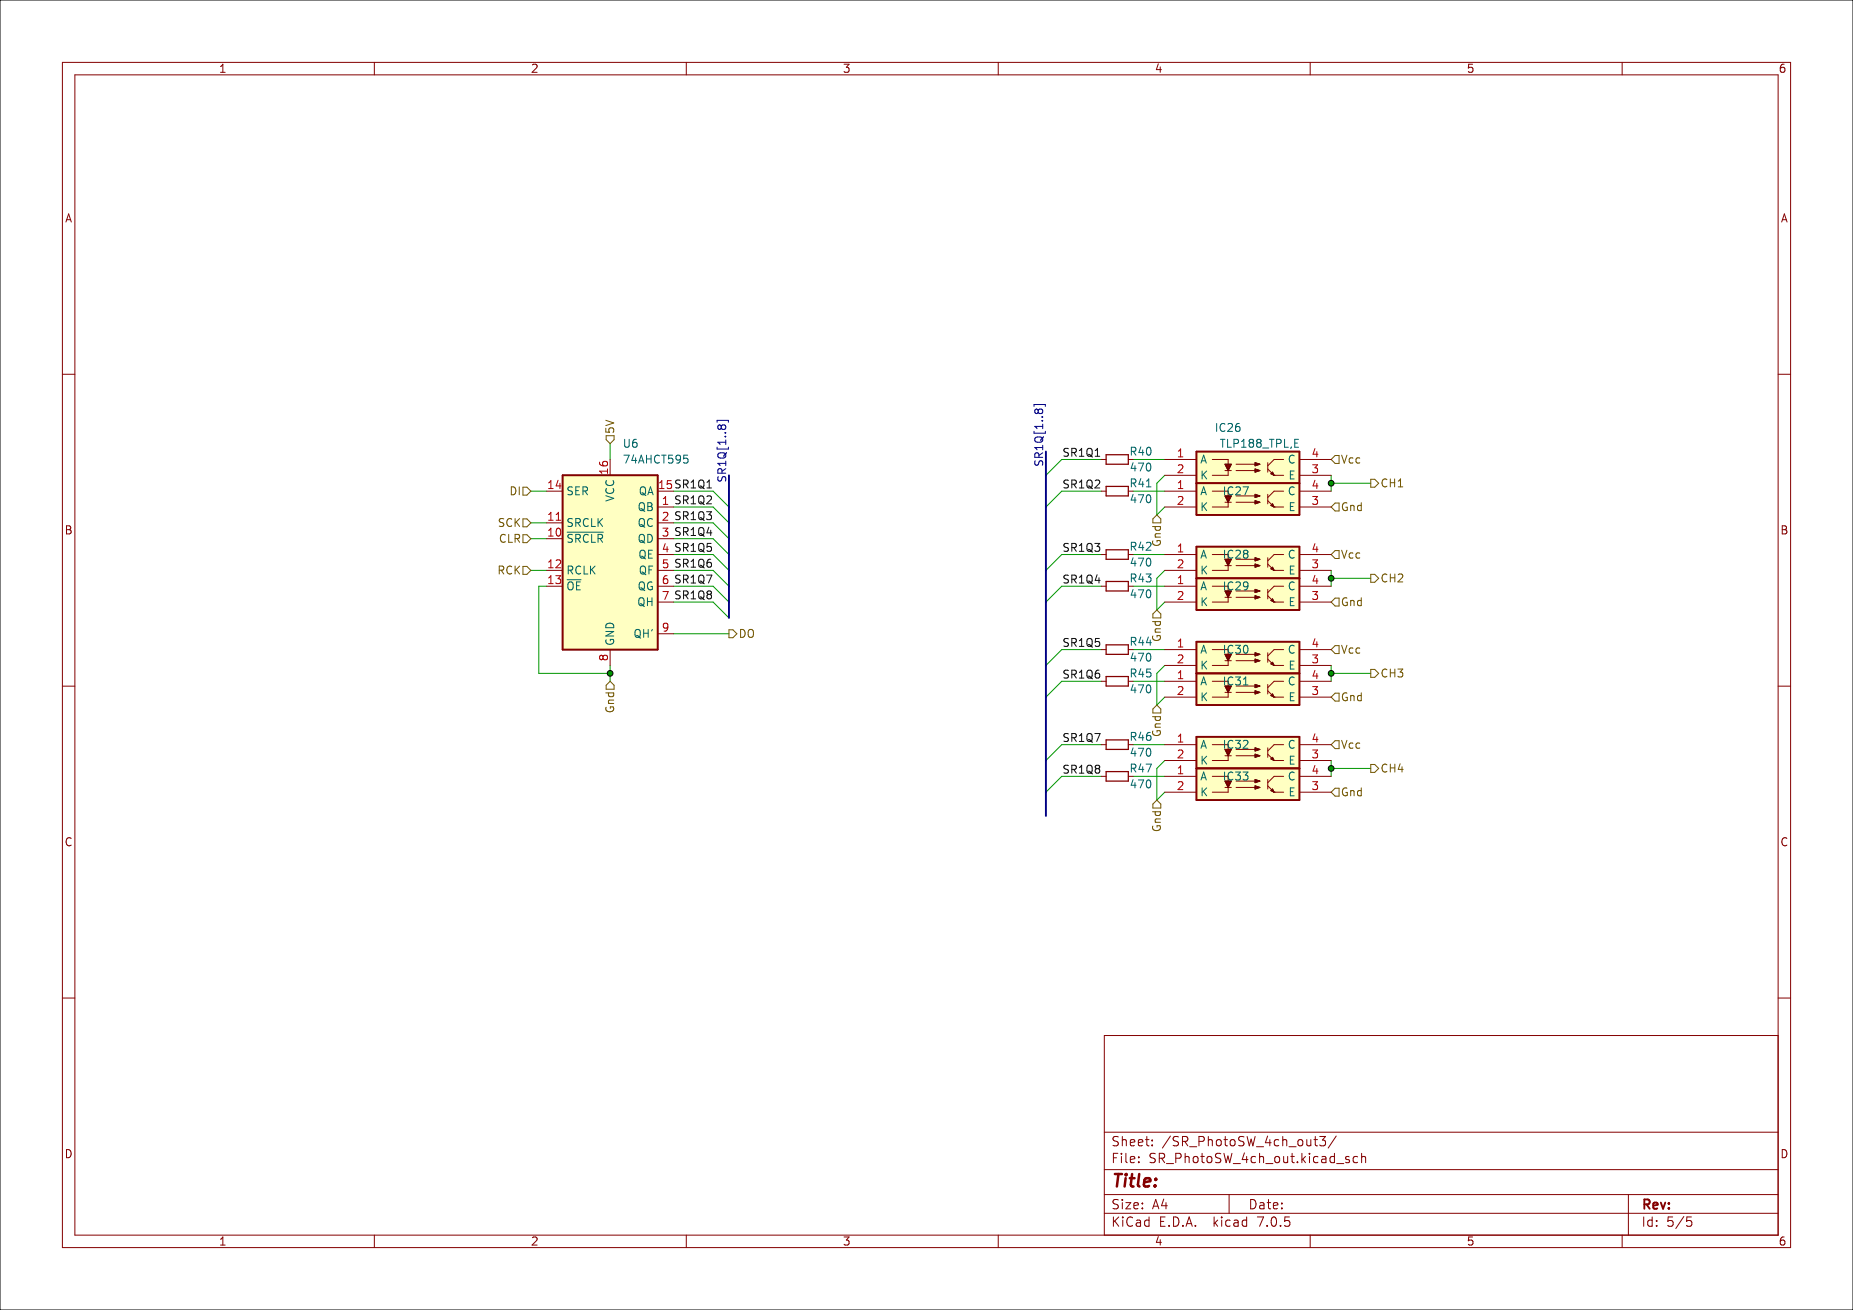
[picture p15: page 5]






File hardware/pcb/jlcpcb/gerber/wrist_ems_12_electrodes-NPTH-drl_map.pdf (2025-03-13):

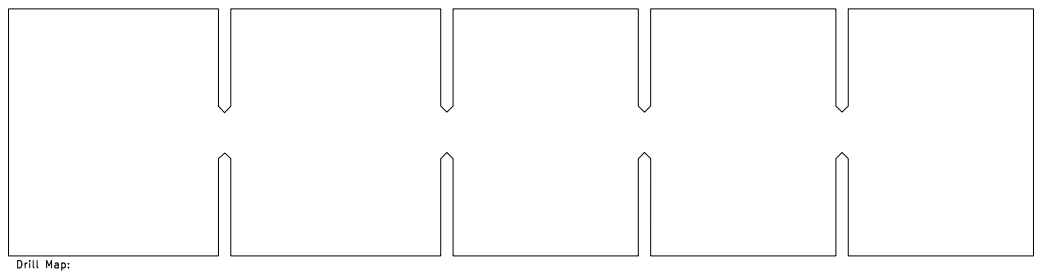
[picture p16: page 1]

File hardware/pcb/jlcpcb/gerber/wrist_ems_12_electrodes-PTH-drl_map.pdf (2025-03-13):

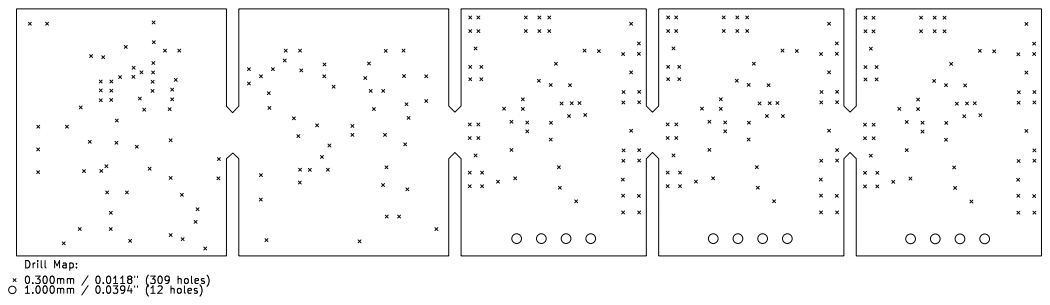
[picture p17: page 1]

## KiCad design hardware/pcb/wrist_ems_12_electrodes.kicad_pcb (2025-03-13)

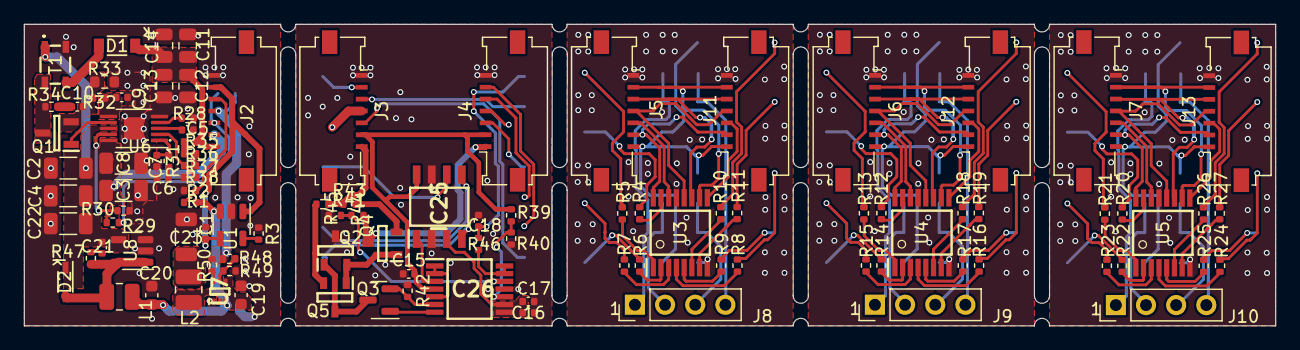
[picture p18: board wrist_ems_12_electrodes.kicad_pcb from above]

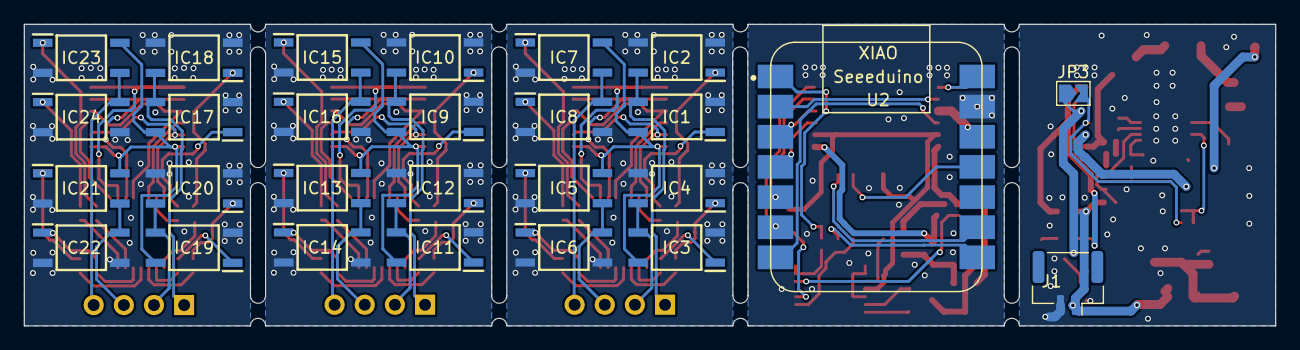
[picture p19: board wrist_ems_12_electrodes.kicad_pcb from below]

Board: 2 copper layers, 105.4 x 25.4 mm, 131 parts (27 on the bottom side), 140 nets.

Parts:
C1, C18: 1nF; C_0402_1005Metric
C2, C3, C4, C8, C22, C23: 47uF; C_1206_3216Metric
C5: 0.1uF; C_0402_1005Metric
C6: 22nF; C_0402_1005Metric
C7: 100pF; C_0402_1005Metric
C9: 10nF; C_0402_1005Metric
C10: 220pF; C_0402_1005Metric
C11, C12, C13, C14: 100nF; C_0805_2012Metric
C15, C16: 100nF; C_0402_1005Metric
C17: 10uF; C_0402_1005Metric
C19, C20: 4.7uF; C_0603_1608Metric
C21: 120pF; C_0402_1005Metric
D1: RF081MM2STR
D2: NSVR1020MW2T1G; SOD2512X110N
IC1, IC2, IC3, IC4, IC5, IC6, IC7, IC8, IC9, IC10, IC11, IC12, IC13, IC14, IC15, IC16, IC17, IC18, IC19, IC20, IC21, IC22, IC23, IC24: TLP188_TPL,E; SOP254P700X220-4N
IC25: DAC8830ID; SOIC127P600X175-8N
IC26: OPA4205APWT; SOP65P640X120-14N
J1: Conn_01x02_Pin; JST_GH_SM02B-GHS-TB_1x02-1MP_P1.25mm_Horizontal
J2, J3, J4, J5, J6, J7, J11, J12, J13: Conn_01x07_Pin; Molex_200528-0070_1x07-1MP_P1.00mm_Horizontal
J8, J9, J10: Conn_01x04_Pin; PinHeader_1x04_P2.54mm_Vertical
JP3: Jumper_2_Open; SolderJumper-2_P1.3mm_Open_TrianglePad1.0x1.5mm
L1: 4.7uH; L_1008_2520Metric
L2: 1uH; L_1008_2520Metric
Q1: RSR030N06TL; SOT95P280X100-3N
Q2, Q4, Q5: MMBTA92LT1G; SOT96P237X111-3N
Q3: DMN30H4D0L; SOT-23
R1, R2, R29, R49: 100k; R_0402_1005Metric
R3: 10k; R_0402_1005Metric
R4, R5, R6, R7, R8, R9, R10, R11, R12, R13, R14, R15, R16, R17, R18, R19, R20, R21, R22, R23, R24, R25, R26, R27: 330; R_0402_1005Metric
R28: 130k(100kHz); R_0402_1005Metric
R30: 240k; R_0402_1005Metric
R31: 6.8k; R_0402_1005Metric
R32, R34, R47: 22; R_0402_1005Metric
R33: 0.02; R_0603_1608Metric
R35, R36, R37, R50: 499k; R_0402_1005Metric
R38: 16k; R_0402_1005Metric
R39: 300k; R_0402_1005Metric
R40: 200k; R_0402_1005Metric
R41: 1k; R_0402_1005Metric
R42: 1k3; R_0402_1005Metric
R43, R46: 100; R_0402_1005Metric
R44: 1M; R_0402_1005Metric
R45: 30k; R_0402_1005Metric
R48: 453k; R_0402_1005Metric
T1: ATB322515-0110-T000; ATB3225150110T000
U1: MCP73812T-420I-OT; SOT-23-5
U2: SeeeduinoXIAO_onlyPinHeader; XIAO-nRF52840-Sense-14P-2.54-21X17.8MM)_onlyPins
U3, U4, U5: 74AHCT595; SOP65P640X110-16N
U6: LT3757AEMSE; MSOP-10-1EP_3x3mm_P0.5mm_EP1.68x1.88mm
U7: XPS62A01DRLR; SOTFL50P160X60-6N
U8: TPS613222ADBV; SOT-23-5

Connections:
3V3: J3.4, U2.12 (3V3)
5V: C15.2, IC25.8 (VDD), IC26.4 (V+), J3.6, J4.2, R39.2
150V: J3.7, R41.1, R43.1
/SR_PhotoSW_4ch_out1/CH1: IC9.3 (E), IC10.4 (C), J9.1
/SR_PhotoSW_4ch_out1/CH2: IC11.3 (E), IC12.4 (C), J9.2
/SR_PhotoSW_4ch_out1/CH3: IC13.3 (E), IC14.4 (C), J9.3
/SR_PhotoSW_4ch_out1/CH4: IC15.3 (E), IC16.4 (C), J9.4
/SR_PhotoSW_4ch_out1/SR1Q1: R12.2, U4.15 (QA)
/SR_PhotoSW_4ch_out1/SR1Q2: R13.2, U4.1 (QB)
/SR_PhotoSW_4ch_out1/SR1Q3: R14.2, U4.2 (QC)
/SR_PhotoSW_4ch_out1/SR1Q4: R15.2, U4.3 (QD)
/SR_PhotoSW_4ch_out1/SR1Q5: R16.2, U4.4 (QE)
/SR_PhotoSW_4ch_out1/SR1Q6: R17.2, U4.5 (QF)
/SR_PhotoSW_4ch_out1/SR1Q7: R18.2, U4.6 (QG)
/SR_PhotoSW_4ch_out1/SR1Q8: R19.2, U4.7 (QH)
/SR_PhotoSW_4ch_out2/CH1: IC17.3 (E), IC18.4 (C), J10.1
/SR_PhotoSW_4ch_out2/CH2: IC19.3 (E), IC20.4 (C), J10.2
/SR_PhotoSW_4ch_out2/CH3: IC21.3 (E), IC22.4 (C), J10.3
/SR_PhotoSW_4ch_out2/CH4: IC23.3 (E), IC24.4 (C), J10.4
/SR_PhotoSW_4ch_out2/SR1Q1: R20.2, U5.15 (QA)
/SR_PhotoSW_4ch_out2/SR1Q2: R21.2, U5.1 (QB)
/SR_PhotoSW_4ch_out2/SR1Q3: R22.2, U5.2 (QC)
/SR_PhotoSW_4ch_out2/SR1Q4: R23.2, U5.3 (QD)
/SR_PhotoSW_4ch_out2/SR1Q5: R24.2, U5.4 (QE)
/SR_PhotoSW_4ch_out2/SR1Q6: R25.2, U5.5 (QF)
/SR_PhotoSW_4ch_out2/SR1Q7: R26.2, U5.6 (QG)
/SR_PhotoSW_4ch_out2/SR1Q8: R27.2, U5.7 (QH)
/SR_PhotoSW_4ch_out/CH1: IC1.3 (E), IC2.4 (C), J8.1
/SR_PhotoSW_4ch_out/CH2: IC3.3 (E), IC4.4 (C), J8.2
/SR_PhotoSW_4ch_out/CH3: IC5.3 (E), IC6.4 (C), J8.3
/SR_PhotoSW_4ch_out/CH4: IC7.3 (E), IC8.4 (C), J8.4
/SR_PhotoSW_4ch_out/SR1Q1: R4.2, U3.15 (QA)
/SR_PhotoSW_4ch_out/SR1Q2: R5.2, U3.1 (QB)
/SR_PhotoSW_4ch_out/SR1Q3: R6.2, U3.2 (QC)
/SR_PhotoSW_4ch_out/SR1Q4: R7.2, U3.3 (QD)
/SR_PhotoSW_4ch_out/SR1Q5: R8.2, U3.4 (QE)
/SR_PhotoSW_4ch_out/SR1Q6: R9.2, U3.5 (QF)
/SR_PhotoSW_4ch_out/SR1Q7: R10.2, U3.6 (QG)
/SR_PhotoSW_4ch_out/SR1Q8: R11.2, U3.7 (QH)
/dcdc_5v_to_100V/Rsense: C10.2, Q1.2, R32.1, R33.2
/dcdc_5v_to_100V/Sense: C9.1, R32.2, U6.6 (SENSE)
/dcdc_5v_to_100V/dcdc_150V_SW: Q1.3, R34.1, T1.4
/dcdc_bat_to_3v3_5v/PG_3V3: R50.1, U7.6 (PG)
/dcdc_bat_to_3v3_5v/dcdc_3V3_SW: L2.1, U7.2 (SW)
/vol_to_curr/2V: C16.2, C17.2, IC25.3 (VREF), IC26.8, IC26.9 (-)
CLR: J4.6, U2.6 (PA9_A5_D5_SCL)
CUR_OUT: J4.1, Q4.3 (C), R44.1
CUR_vol: C18.2, R46.2, U2.1 (PA02_A0_D0)
DAC_MOSI: IC25.6 (SDI), U2.11 (PA6_A10_D10_MOSI)
DAC_SCK: IC25.5 (SCLK), U2.9 (PA7_A8_D8_SCK)
DAC_nCS: IC25.4 (~CS), U2.8 (PB09_A7_D7_RX)
DI: J4.3, U2.4 (PA11_A3_D3)
EN_150V: J3.5, U2.7 (PB08_A6_D6_TX)
GND: C15.1, C16.1, C17.1, C18.1, IC25.2 (AGND), IC25.7 (DGND), IC26.11 (V-), J3.1, J4.7, Q2.3 (C), R40.2, R42.2, R45.2, U2.13 (GND)
GNDA: C1.1, C2.2, C3.2, C4.2, C5.2, C6.2, C7.2, C8.2, C9.2, C11.2, C12.2, C13.2, C14.2, C19.2, C20.2, C22.2, C23.2, J1.2, J2.7, R2.2, R3.2, R28.1, R30.2, R33.1, R38.1, R49.2, T1.2, U1.2 (V_{SS}), U6.5 (SYNC), U6.11 (GND), U7.1 (GND), U8.2 (GND), U8.3 (NC)
unnamed: C6.1, R31.2
unnamed: C10.1, R34.2
unnamed: C21.1, R47.1
unnamed: D1.2 (A), T1.3
unnamed: D2.2 (A), L1.2, R47.2, U8.1 (SW), U8.5 (NC)
unnamed: IC1.1 (A), R4.1
unnamed: IC2.1 (A), R5.1
unnamed: IC3.1 (A), R6.1
unnamed: IC4.1 (A), R7.1
unnamed: IC5.1 (A), R8.1
unnamed: IC6.1 (A), R9.1
unnamed: IC7.1 (A), R10.1
unnamed: IC8.1 (A), R11.1
unnamed: IC9.1 (A), R12.1
unnamed: IC10.1 (A), R13.1
unnamed: IC11.1 (A), R14.1
unnamed: IC12.1 (A), R15.1
unnamed: IC13.1 (A), R16.1
unnamed: IC14.1 (A), R17.1
unnamed: IC15.1 (A), R18.1
unnamed: IC16.1 (A), R19.1
unnamed: IC17.1 (A), R20.1
unnamed: IC18.1 (A), R21.1
unnamed: IC19.1 (A), R22.1
unnamed: IC20.1 (A), R23.1
unnamed: IC21.1 (A), R24.1
unnamed: IC22.1 (A), R25.1
unnamed: IC23.1 (A), R26.1
unnamed: IC24.1 (A), R27.1
unnamed: IC25.1 (VOUT), IC26.3 (+)
unnamed: IC26.1, IC26.2 (-), IC26.5 (+)
unnamed: IC26.6 (-), Q3.2 (S), R42.1
unnamed: IC26.10 (+), R39.1, R40.1
unnamed: IC26.12 (+), R44.2, R45.1
unnamed: IC26.13 (-), IC26.14, R46.1
unnamed: Q2.1 (B), Q3.3 (D), Q5.3 (C)
unnamed: Q2.2 (E), Q4.1 (B), Q5.1 (B)
unnamed: IC26.7, Q3.1 (G)
unnamed: Q4.2 (E), R43.2
unnamed: Q5.2 (E), R41.2
unnamed: R35.1, R36.2
unnamed: R36.1, R37.2
unnamed: R3.1, U1.5 (PROG)
unnamed: R37.1, R38.2, U6.2 (FBX)
unnamed: Q1.1, U6.7 (GATE)
unnamed: R28.2, U6.4 (RT)
unnamed: C5.1, U6.3 (SS)
unnamed: C7.1, R31.1, U6.1 (VC)
unnamed: R29.1, R30.1, U6.9 (~SHDN/UVLO)
unnamed: R48.2, R49.1, U7.5 (FB)
RCK: J4.4, U2.3 (PA10_A2_D2)
SCK: J4.5, U2.5 (PA8_A4_D4_SDA)
Vbat: C19.1, C20.1, J1.1, L1.1, R1.1, U1.3 (V_{BAT}), U7.3 (VIN), U7.4 (EN)
bat_vol: J3.3, U2.2 (PA4_A1_D1)
dcdc_3V3: C23.1, J2.4, JP3.1 (A), L2.2, R48.1, R50.2
dcdc_5V: C2.1, C3.1, C4.1, C8.1, C21.2, C22.1, D2.1 (K), J2.2, T1.1, U6.8 (INTVCC), U6.10 (VIN), U8.4 (VOUT)
dcdc_150V: C11.1, C12.1, C13.1, C14.1, D1.1 (K), J2.1, R35.2
dcdc_EN_150V: J2.3, JP3.2 (B), R29.2
dcdc_bat_vol: J2.5, R1.2, R2.1
dcdc_usb_5V: C1.2, J2.6, U1.1 (CE), U1.4 (V_{DD})
sw1_5v: J5.6, J11.2, U3.16 (VCC)
sw1_clr: J5.2, J11.6, U3.10 (~SRCLR)
sw1_di: J5.5, U3.14 (SER)
sw1_do: J11.3, U3.9 (QH')
sw1_gnd: IC1.2 (K), IC2.2 (K), IC2.3 (E), IC3.2 (K), IC4.2 (K), IC4.3 (E), IC5.2 (K), IC6.2 (K), IC6.3 (E), IC7.2 (K), IC8.2 (K), IC8.3 (E), J5.1, J11.7, U3.8 (GND), U3.13 (~OE)
sw1_rck: J5.4, J11.4, U3.12 (RCLK)
sw1_sck: J5.3, J11.5, U3.11 (SRCLK)
sw1_vcc: IC1.4 (C), IC3.4 (C), IC5.4 (C), IC7.4 (C), J5.7, J11.1
sw2_5v: J6.6, J12.2, U4.16 (VCC)
sw2_clr: J6.2, J12.6, U4.10 (~SRCLR)
sw2_di: J6.5, U4.14 (SER)
sw2_gnd: IC9.2 (K), IC10.2 (K), IC10.3 (E), IC11.2 (K), IC12.2 (K), IC12.3 (E), IC13.2 (K), IC14.2 (K), IC14.3 (E), IC15.2 (K), IC16.2 (K), IC16.3 (E), J6.1, J12.7, U4.8 (GND), U4.13 (~OE)
sw2_rck: J6.4, J12.4, U4.12 (RCLK)
sw2_sck: J6.3, J12.5, U4.11 (SRCLK)
sw2_vcc: IC9.4 (C), IC11.4 (C), IC13.4 (C), IC15.4 (C), J6.7, J12.1
sw3_5v: J7.6, J13.2, U5.16 (VCC)
sw3_clr: J7.2, J13.6, U5.10 (~SRCLR)
sw3_di: J7.5, U5.14 (SER)
sw3_do: J13.3, U5.9 (QH')
sw3_gnd: IC17.2 (K), IC18.2 (K), IC18.3 (E), IC19.2 (K), IC20.2 (K), IC20.3 (E), IC21.2 (K), IC22.2 (K), IC22.3 (E), IC23.2 (K), IC24.2 (K), IC24.3 (E), J7.1, J13.7, U5.8 (GND), U5.13 (~OE)
sw3_rck: J7.4, J13.4, U5.12 (RCLK)
sw3_sck: J7.3, J13.5, U5.11 (SRCLK)
sw3_vcc: IC17.4 (C), IC19.4 (C), IC21.4 (C), IC23.4 (C), J7.7, J13.1
sw_do: J12.3, U4.9 (QH')
usb_5V: J3.2, U2.14 (5V)

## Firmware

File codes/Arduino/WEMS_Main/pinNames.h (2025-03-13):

/** Pin name aliases
 *  
 *      somwhow "int PIN_VOL_CUR = P0_2;" or so didn't work well. so here I defined them using #define macro. 
 *      if you find a better way, please modify it.
 */
#ifndef PIN_NAMES_H
#define PIN_NAMES_H

#define  PIN_VOL_CUR    P0_2    //A0;
#define  PIN_VOL_BAT    P0_3    //A1;

#define  PIN_SR_RCK     P0_28   //D2;
#define  PIN_SR_DIN     P0_29   //D3;
#define  PIN_SR_SCK     P0_4    //D4;
#define  PIN_SR_CLR     P0_5    //D5;

#define  PIN_HiV_EN     P1_11   //D6;

//#define  PIN_DAC_SDA    P0_4    //D4;
//#define  PIN_DAC_SCL    P0_5    //D5;

#define  PIN_DAC_MOSI   P1_15    //D10;
#define  PIN_DAC_MISO   P1_14    //D9;
#define  PIN_DAC_SCK    P1_13    //D8;
#define  PIN_DAC_nCS    P1_12    //D7;

//#define  PIN_NC P1_14
#define  PIN_NC P0_5

#endif

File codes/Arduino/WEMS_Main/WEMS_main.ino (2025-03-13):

#include <ArduinoBLE.h>

/*
     For timer interruption
*/
#define TIMER_INTERRUPT_DEBUG         0
#define _TIMERINTERRUPT_LOGLEVEL_     0
#include "NRF52_MBED_TimerInterrupt.h"
NRF52_MBED_Timer ITimer(NRF_TIMER_3);

/*
    For multi-task
*/
#include <Scheduler.h>

/*
    For EMS
*/
#include "pinNames.h"
#include "WEMS_PulseControl.h"
EMSControl* ems;

int drum_note;
int drum_stim_flag;

/*
    For BLE
*/
BLEDevice central;
BLEService myService("19b10000-e9f3-537e-4f6c-d104768a1214");
//BLEStringCharacteristic intensityCharacteristic("19b10001-e9f3-537e-4f6c-d104768a1214", BLEWrite | BLERead, 20);
//BLEStringCharacteristic pulseWidthCharacteristic("19b10002-e9f3-537e-4f6c-d104768a1214", BLEWrite | BLERead, 20);
//BLEStringCharacteristic frequencyCharacteristic("19b10003-e9f3-537e-4f6c-d104768a1214", BLEWrite | BLERead, 20);
BLEStringCharacteristic startCharacteristic("19b10004-e9f3-537e-4f6c-d104768a1214", BLEWrite | BLERead, 200);

void led_blink(void);
void bat_read(void);
float vol_bat;

/*  --------------------------------------------------------------------
    Command list

    commands is supposed to be received via Serial or BLE
    --------------------------------------------------------------------  */
void execCommand(String command)
{
    /*
        Start/Stop the stimulation with infinit duration
    */
    if (command == "a" && ems->is_stimulating == 0) {
        ems->setStimDuration_inf();
        ems->start();
    } else if (command == "a" && ems->is_stimulating == 1) {
        ems->stop();
    }
    /*
        Start the stimulation with infinit duration. 
        This is the same fuction as "a" when stimulation is not started.
        This will not stop stimulation as "a". 
    */
    else if (command.startsWith("start")) {
        ems->setStimDuration_inf();
        ems->start();
    }
    /*
        Start the stimulation.
           If an integer argument is followed, it is used to define the stimulation duration in the same way as the command "dur millis"
           If no argument is followed, the stimulation duration is set at 0, which means stimulation lasts until the commands "stop"/"a" are sent.

           ex1. stim1000 is sent, stimulation lasts for 1 second (1000 ms)
           ex2. stim (or stim0) are sent, the last duration is kept.
    */
    else if (command.startsWith("stim")) {
        //set stimulation duration [ms]
        int tmp = command.substring(4).toInt();
        ems->setStimDuration_us(tmp * 1000);
        ems->start();
    }
    /*
        Stop the stimulation.
    */
    else if (command.startsWith("stop")) {
        ems->stop();
    }
    /*
        Define the intensity. Float is acceptable. the Unit is [mA]. The maximum is "15"
        ex1, if "int15" is sent, the intensity will be 15mA (100% of the max)
        ex2, if "int5" is sent, the intensity will be 5 mA (5/15 * 100% of the max)
    */
    else if (command.startsWith("int")) {//**int**ensity 0~15[mA]
        float tmp  = command.substring(3).toFloat();
        ems->setIntensity(tmp);
    }
    /*
        Define the frequency.
        Due to the loop is slow, the frequency is limited to around 1~400 Hz
    */
    else if (command.startsWith("freq")) {
        int tmp  = command.substring(4).toInt();
        ems->setFrequency(tmp);
        ITimer.setInterval(ems->getPeriod(), ems->pulse_rise_timing);
    }
    /*
        Define the pulse width. This can be changed by 50 us
        150 ~ 500 us
    */
    else if (command.startsWith("wid")) {
        int tmp = command.substring(3).toInt();
        ems->setPulseWidth(tmp);
    }
    /*
        set stimulation duration (milli sec [ms]) in the same as the function "stim" without starting stimulation
        0 ~ 10000 ms
    */
    else if (command.startsWith("dur ms")) {
        int tmp = command.substring(6).toInt();
        ems->setStimDuration_us(tmp * 1000);
    }
    /*
        set stimulation duration (sec [s])
        0 ~ 10 s
    */
    else if (command.startsWith("dur s")) {
        float tmp = command.substring(5).toFloat();
        ems->setStimDuration_us(tmp * 1000000);
    }
    /*
        set channel from which the stimulation current is output
        1 ~ 12
    */
    else if (command.startsWith("setch")) {
        int tmp = command.substring(5).toInt();
        ems->swboard->setch(tmp);
        if (Serial) {
            Serial.print("channel: ");
            Serial.println(ems->swboard->getch());
        }
    }
    /*
     *  Show the parameters now applied in JSON style via BLE and Serial.
     *  
     *  Without any argument, i.e., if receiving "param", then it dumps all parameter. 
     *  With an argument, it return only the parameter requested.
     *      e.g., "param channel" being received, this return {"channel": 1}
     *      e.g., "param voltage" being received, this return {"voltage": 32}
     *  the means of parameters are:
     *      - "channel":    Returns the currently selected channel.
     *      - "intensity":  Returns the currently selected intensity (hight of a pulse) [mA].
     *      - "voltage":    Returns the last pulse's voltage, which varies by the intensity selected and the impedance of human body.
     *      - "p_width":    Returns the currently selected pulse widht [us]. 
     *                      The pulse width is the width of one phase of the biphasic pulse. 
     *                      Both phase has the same width and the interval bw thethem is around 130 us, so the overall pulse widh will be 2 * p_width + 130 us
     *                      (e.g.) if p_width = 200 us, then overall pulse width should be 530 us
     *      - "frequency":  Returns the currently selected frequency.
     *      - "period":     Returns the currently selected period, which is calculated from the frequency.
     *                      (e.g.) if frequency = 200 Hz, then the period should be 1000000/200 = 50000 us.
     *      - "battery":    Returns the current battery voltage. The valtage, when it fully charged, is around 4.2 V.
     *                      Note that the battery voltage decreases non-linearly. 
     */
    else if (command.startsWith("param")) {
        String tmp = command.substring(5);
        static float const rate_DAC2BAT = (1.0 / 4095.0) * 3.3 * 2;
        tmp.trim();
        String retval = "{\n";
        if (tmp == "" || tmp == "channel")  retval += String("  \"channel\":   ") + ems->swboard->getch() + String(",\n");
        if (tmp == "" || tmp == "intensity")retval += String("  \"intensity\": ") + ems->getIntensity()   + String(" [mA],\n");
        if (tmp == "" || tmp == "voltage")  retval += String("  \"voltage\":   ") + ems->getVoltage()     + String(" [V],\n");
        if (tmp == "" || tmp == "p_width")  retval += String("  \"p_width\":   ") + ems->getPulseWidth()  + String(" [us],\n");
        if (tmp == "" || tmp == "frequency")retval += String("  \"frequency\": ") + ems->getFrequency()   + String(" [Hz],\n");
        if (tmp == "" || tmp == "period")   retval += String("  \"period\":    ") + ems->getPeriod()      + String(" [us],\n");
        if (tmp == "" || tmp == "battery")  retval += String("  \"battery\":   ") + vol_bat*rate_DAC2BAT  + String(" [V],\n"); 
        retval += String("}\n");
        if (central && central.connected() && startCharacteristic) {
            startCharacteristic.writeValue(retval);
        }
        if (Serial) {
            Serial.println(retval);
        }
    }
    /*
        Start/stop drum pattern.
    */
    else if (command == "drum") {
        drum_stim_flag = !drum_stim_flag;
    }
}

void setup() {

    pinMode(LEDR, OUTPUT);
    pinMode(LEDG, OUTPUT);
    pinMode(LEDB, OUTPUT);
    nrf_gpio_cfg_output(LEDR);
    nrf_gpio_cfg_output(LEDG);
    nrf_gpio_cfg_output(LEDB);
    pinMode(PIN_VOL_CUR, INPUT);
    pinMode(PIN_VOL_BAT, INPUT);

    // init Serial
    Serial.begin(9600);

    // init BLE
    while (!BLE.begin()) delay (100);
    BLE.setLocalName("wristEMS02");
    BLE.setAdvertisedService(myService);
    myService.addCharacteristic(startCharacteristic);
    BLE.addService(myService);
    BLE.advertise();

    analogReadResolution(12);
    
    // init EMS
    ems = new EMSControl();
    //set stimulation frequency
    ITimer.attachInterruptInterval(ems->getPeriod(), ems->pulse_rise_timing);
    //ITimer1.attachInterruptInterval(1000000, led_blink);
    //attach a task that render stimulation pulses
    //Scheduler.startLoop(ems->task_pulse);

    digitalWrite(LEDG, LOW);
    delay (1000);
}

void loop() {
    /*
        Used in common for Serial and BLE
    */
    static String command = "";

    /*  -----------------------
        Serial communication
        ----------------------- */
    static int const buff_size = 64;
    static char buff[buff_size];
    static int idx = 0;
    static bool lastconnection = false;
    if (Serial && Serial.available() > 0 ) {
        while (idx < buff_size) {
            buff[idx] = Serial.read();
            if (buff[idx] == '\n') break;
            idx++;
        }
        buff[idx] = '\0';
        command = String(buff);
        Serial.print("input: ");
        Serial.println(command);
        execCommand(command);
        idx = 0;
    }

    /*  -----------------------
        Bluetooth communication
        ----------------------- */
    /*
        Check if a BLE central (phone or watch) is connected
    */
    if (!central) {
        //  if not connected, try to connect.
        central = BLE.central();
    }
    else if (central.connected() && startCharacteristic.written()) {
        if(!lastconnection){
            Serial.println("connected:");
            lastconnection = true;
        }
        //  if connected, read a buffer in string and parse the command.
        command = startCharacteristic.value();
        if (Serial) {
            Serial.print("input: ");
            Serial.println(command);
        }
        execCommand(command);
    }
    else if(!central.connected() && lastconnection){
        lastconnection = false;
        central.disconnect();
        if(Serial) Serial.println("disconnected");
    }
    

    led_blink();
    bat_read();
    ems->task_pulse();

    if (drum_stim_flag == 1) {
        if (ems->is_stimulating == 0) {
            if (drum_note == 0) {
                drum_note++;
            } else if (drum_note == 1) {
                delay(300);
                drum_note++;
            } else if (drum_note == 2) {
                delay(100);
                drum_note++;
            } else if (drum_note == 3) {
                delay(400);
                drum_note = 0;
            }
            
            execCommand("stim 100000");
        }
    }
}

/*
    LED blink
*/
void led_blink()
{
    static unsigned long currentMicros = 0;
    static unsigned long previousMicros = 0;
    static unsigned long const interval = 2000000;
    static int ledState = LOW;

    currentMicros = micros();
    if (currentMicros - previousMicros >= interval) {
        previousMicros = currentMicros;
        ledState = !ledState;
        
        digitalWrite(LEDG, ledState);
        digitalWrite(LEDB, !ledState);
    }
}

/*
    Battery's voltage check
*/
void bat_read()
{
    static unsigned long currentMicros = 0;
    static unsigned long previousMicros = 0;
    static unsigned long const interval = 5000000;

    currentMicros = micros();
    if (currentMicros - previousMicros >= interval) {
        previousMicros = currentMicros;
        vol_bat = analogRead(PIN_VOL_BAT);
    }
}

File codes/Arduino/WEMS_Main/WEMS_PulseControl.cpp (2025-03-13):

#include "WEMS_PulseControl.h"

EMSControl* EMSControl::self = NULL;

EMSControl::EMSControl(float arg_intensity, unsigned long arg_pulsewidth, unsigned long arg_frequency)
{
    pinMode(PIN_HiV_EN, OUTPUT);
    this->self = this;
    
    /*
     * DAC inir
     * In Ver.3, DAC is Texas Instruments' DAC8830, which is controlled via SPI. 
     * 16 bit, 50 MHz
    */
    SPI.begin();
    pinMode(PIN_DAC_nCS, OUTPUT);
    digitalWrite(PIN_DAC_nCS, HIGH);
    //mbed-enable library limit SPI speed 8MHz, while the other library limit it 32MHz
    //the DAC can be 50MHz at max, though
    SPI.beginTransaction(SPISettings(8000000, MSBFIRST, SPI_MODE0));
    nrf_gpio_pin_clear(PIN_DAC_nCS);
    SPI.transfer16(0);
    nrf_gpio_pin_set  (PIN_DAC_nCS);
    SPI.endTransaction();
    
    /*
     *  Init Switching Board
     */
    this->swboard = new SWBoard();
    this->swboard->resetch();

    /*
     *  Init stimulation parameters
     */
    for (int i = 0; i < 12; i++){
        this->val_intensity[i] = arg_intensity;
        this->intensity_voltage[i] = 0;
    }
    this->val_pulseWidth = arg_pulsewidth;
    this->val_frequency = arg_frequency;
    this->val_period = 1000000 / this->val_frequency;

    /*
     *  Init timing vars
     */
    this->stim_duration = 1000000; //1sec
    this->previousMicros_stim_duration = micros();
    this->pulse_rise = 0;
    this->is_stimulating = 0;

    pinMode(PIN_NC, OUTPUT);
}


void EMSControl::pulse_rise_timing(void)
{
    if (EMSControl::self == NULL) return;
    self->pulse_rise = 1;
}

void EMSControl::task_pulse(void)
{
    static unsigned long currentMicros = 0;
    static bool l_lock = false;
    

    if (EMSControl::self == NULL) return;
    if (self->is_stimulating != 1) return;
    if (l_lock) return;
    l_lock = true;
    
    currentMicros = micros();

    if (self->pulse_rise == 1) {
        self->pulse();  //anodic
        self->swboard->setpol(1); //set pol cathode for next pulse();
        //delayMicroseconds(10); // wait for the swboard being set completely
        self->pulse();  //cathodic
        self->swboard->setpol(0); //set pol anode for next pulse();

        self->pulse_rise = 0;
    }

    /*
        If stimulation duration is set >0, stop the stimulation after the duration has elapsed.
    */
    if (self->stim_duration > 0 && currentMicros - self->previousMicros_stim_duration >= self->stim_duration) {
        
        SPI.beginTransaction(SPISettings(50000000, MSBFIRST, SPI_MODE0));
        nrf_gpio_pin_clear(PIN_DAC_nCS);
        SPI.transfer16(0);
        nrf_gpio_pin_set  (PIN_DAC_nCS);
        SPI.endTransaction();
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
